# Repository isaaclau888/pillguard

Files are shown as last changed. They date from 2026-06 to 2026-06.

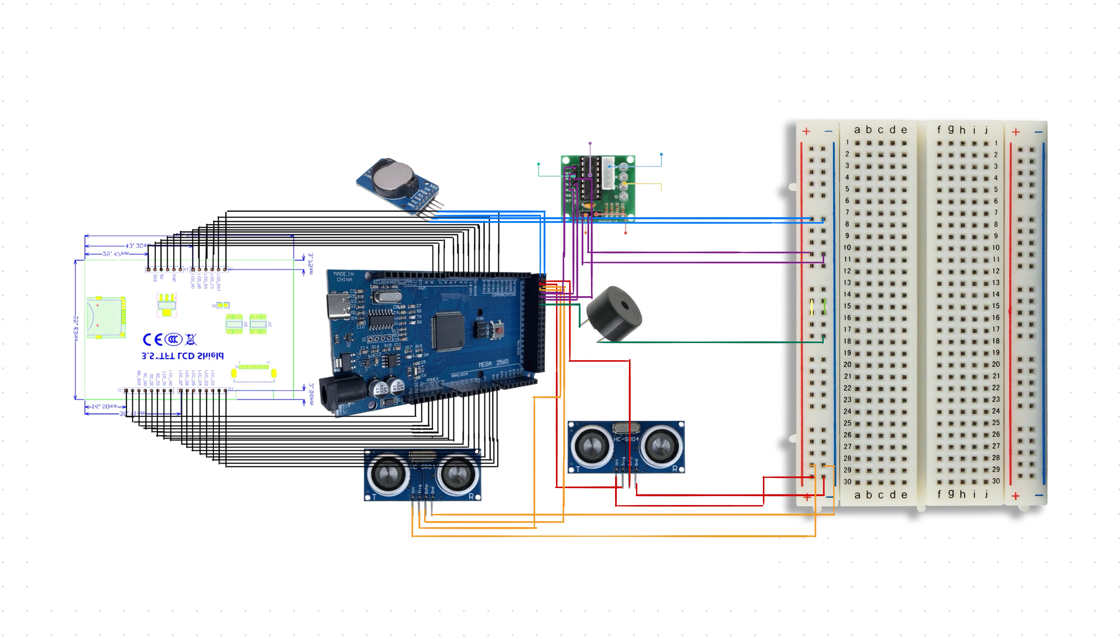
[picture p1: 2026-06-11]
PillGuard Wiring Diagram/PillGuard Wiring Diagram.jpg

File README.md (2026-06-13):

# PillGuard
Have you ever wanted to build a pill dispenser for yourself or your family?
For me, the answer is yes!

So here comes PillGuard, a pill dispenser that keeps track of and tells you when to take your pills. 
This is a completely open-source project. All the 3D parts and the BOM list are in the folders. You may customise my project. 

## How to build it
Please print all the 3D parts. <p>
螢幕截圖 2026-06-11 下午5 09 00 <p>
First, try placing the bottom part with the HC‑SR04 sensor in it. <p>

螢幕截圖 2026-06-11 下午5 09 55 <p>
Secondly, place the middle part with the 28BYJ-48 Stepper Motor + ULN2003 Driver and another HC‑SR04 sensor. <p>

螢幕截圖 2026-06-11 下午5 10 14 <p>
Thirdly, place the spinning system above the 28BYJ-48 Stepper Motor. <p>

螢幕截圖 2026-06-11 下午5 10 55 <p>
Last but not least, put the cover on top of the bottom part with the 3.5-inch screen and Arduino Mega 2560(The blue shaded place is where you place the screen and the Arduino Board).

# Wiring Diagram 
PillGuard Wiring Diagram

Screen: Just follow the diagram. <p>
DS3231 RTC (Real-Time Clock): VCC -> Breadboard (+) Red Rail, GND -> Breadboard (-) Blue Rail, Trig -> Arduino Mega 2560 Pin 20, Echo -> Arduino Mega 2560 Pin 21 <p>
HC-SR04(Cup Sensor): VCC -> Breadboard (+) Red Rail, GND -> Breadboard (-) Blue Rail, Trig -> Arduino Mega 2560 Pin 22, Echo -> Arduino Mega 2560 Pin 23 <p>
HC-SR04(Pill Drop Sensor): VCC -> Breadboard (+) Red Rail, GND -> Breadboard (-) Blue Rail, Trig -> Arduino Mega 2560 Pin 24, Echo -> Arduino Mega 2560 Pin 25 <p>
ULN2003(Steeper Motor Driver): VCC -> Breadboard (+) Red Rail, GND -> Breadboard (-) Blue Rail, IN1 -> Arduino Mega 2560 Pin 26, IN2 -> Arduino Mega 2560 Pin 27, IN3 -> Arduino Mega 2560 Pin 28, IN4 -> Arduino Mega 2560 Pin 29 <p>
Buzzer: Positive(+) -> Arduino Mega 2560 Pin 30, Negative(-) -> Breadboard (-) Blue Rail 

## Why this project actually exists
The reason why this project exists is that the HKDSE 2026 DAT SBA required students to make a  device for medication management and facilitation of medication taking.

Design Problem:
Design and make a device for medication management and facilitation of medication taking.
This device must satisfy the following requirements:
(a) Store at least five different pills separately, allow patients to set different dosages and medication times for each pill, and automatically dispense the required quantity of pills at the right time, for a period of at least one week;
(b) Provide medication reminders to patients in a variety of ways at a predetermined time until the patient confirms that the medication has been taken;
(c) Include a function that automatically provides the right amount of water to drink when it is time to take the medicine;
(d) Add a function that provides practical value to the patients. (For example, properly preserving the medicine.)

But I removed the part (c) feature in this project.

## How I made it
Guess how I made it. I made it by using Fusion 360, which is a completely free CAD app for students. The reason why I made this is that I want to make people not hate taking medicine. By using the dispenser, you can interact with it, making it more fun when you're ill. 

SBA_2026-Apr-05_04-36-30AM-000_CustomizedView2692837445_png

## How to use it?
The question you may ask is how to use this pill dispenser. To use this dispenser, you must set a timer on the app and select which medicine you're taking. For example, at 1 pm, I need to take 2 Panadol Pills. Then it will follow your instructions and do the task at 1 pm.

## Fallout Zine
PillGuard Fallout Zine

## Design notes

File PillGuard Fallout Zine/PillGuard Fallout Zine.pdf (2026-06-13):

# Time to takePILLS!

# PillGuard

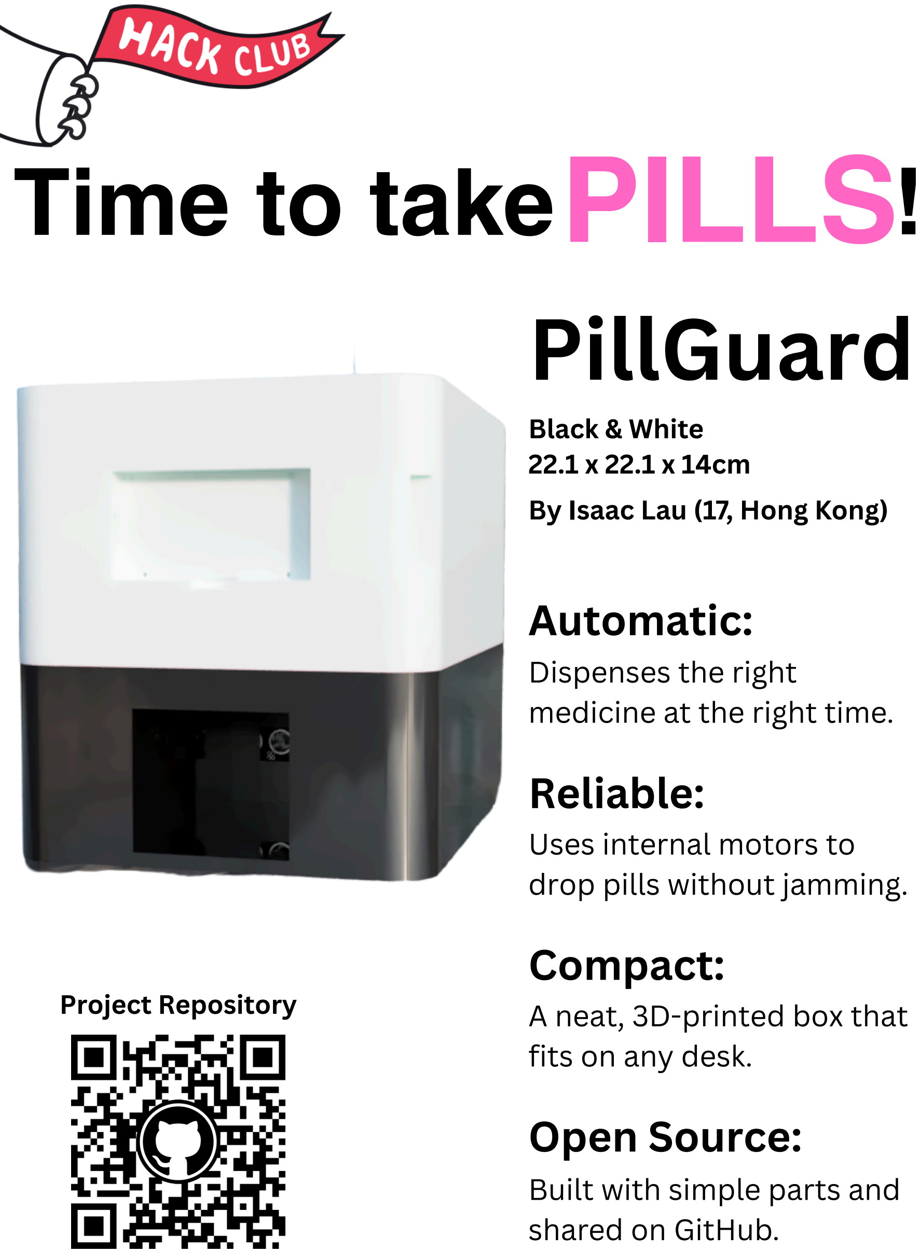
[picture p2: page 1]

Black & White

### 22.1 x 22.1 x 14cm

By Isaac Lau (17, Hong Kong)

Project Repository | Automatic:
Dispenses the right
medicine at the right time.

## Reliable:

Uses internal motors to
drop pills without jamming.

## Compact:

A neat, 3D-printed box that fits on any desk.

## Open Source:

Built with simple parts and shared on GitHub.

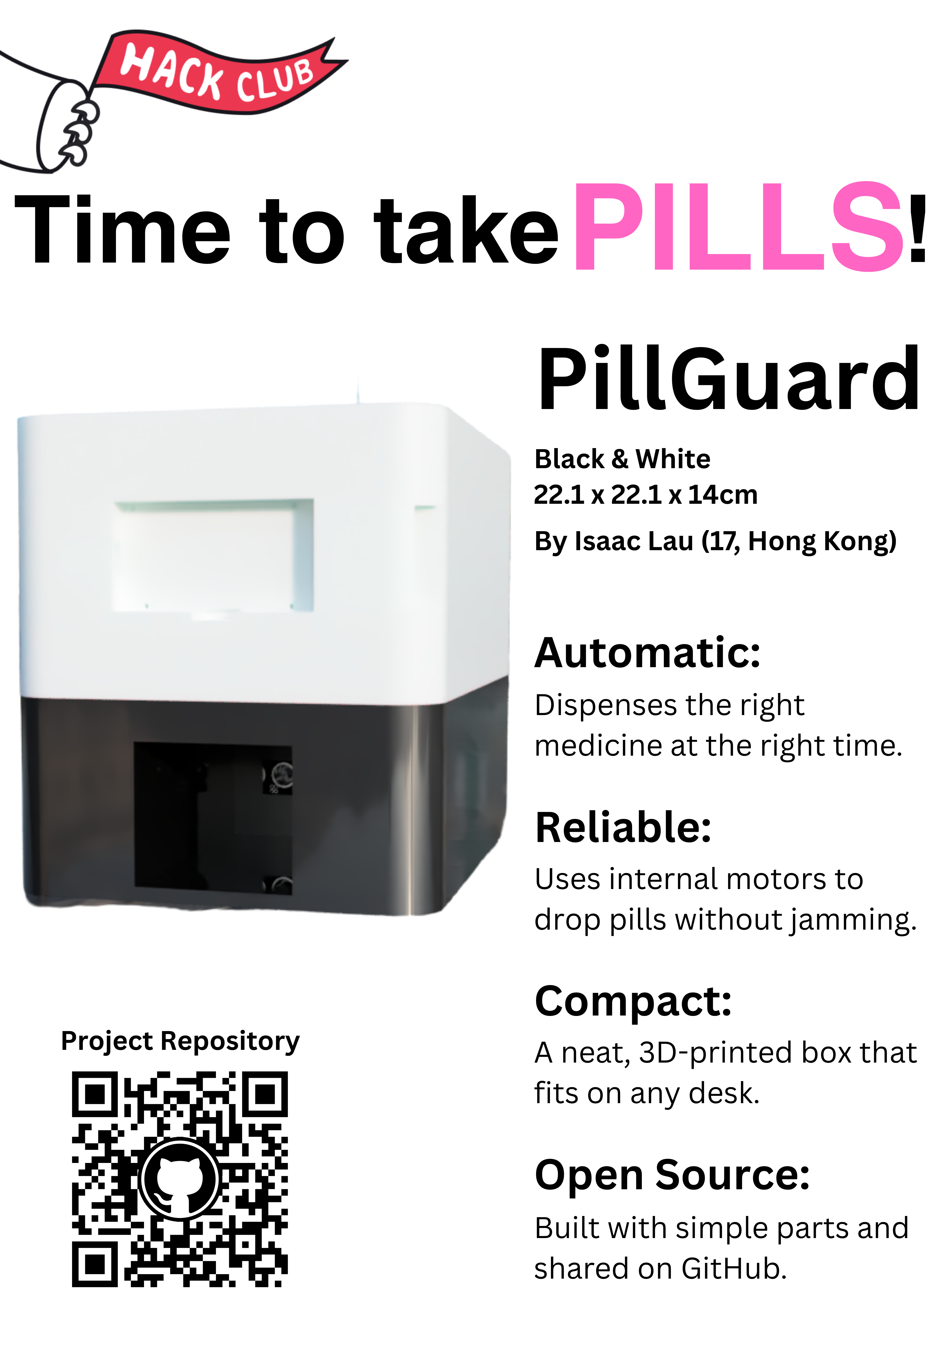
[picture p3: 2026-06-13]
PillGuard Fallout Zine/PillGuard Fallout Zine.png

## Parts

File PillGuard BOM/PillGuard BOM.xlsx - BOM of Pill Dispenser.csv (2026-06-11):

Description | Item | Usage Count | Purchase Quantity | Unit Price | Subtotal | Price(HKD) [$] | Price(RMB) [$] | Price(USD) [$] | Link | Additional description
Electrical Components
Arduino Mega 2560 R3 Type-C (CH340G) |  | 1 | 1 | $98.00 | $98.00 | $98.00 | $86.06 | $12.5 | https://hkstem.club/products/arduino-mega-2560?variant=47304128004391
3.5-inch TFT color screen module, 320x480 ultra-high-definition LCD screen |  | 1 | 1 | $43.32 | $43.32 | $43.32 | $37.50 | $5.53 | https://item.taobao.com/item.htm?id=619917753133
DS3231 RTC Module(Contains Battery) |  | 1 | 1 | $22.05 | $22.05 | $22.05 | $19.36 | $2.81 | https://detail.tmall.com/item.htm?ali_trackid=318_1513cffd14e591e2467183ac4e19fa0b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
28BYJ-48 Stepper Motor + ULN2003 Driver |  | 1 | 1 | $7.06 | $7.06 | $7.06 | $6.20 | $0.90 | https://item.taobao.com/item.htm?abbucket=10&id=682229618612&ns=1&priceTId=2100c90417752809138194116e0ce1&skuId=5076592483944&xxc=taobaoSearch
HC-SR04 Ultrasonic Sensor |  | 2 | 2 | $2.55 | $5.09 | $5.09 | $4.40 | $0.65 | https://item.taobao.com/item.htm?abbucket=10&id=863862858419&ns=1&priceTId=2100c90417752812554093218e0ce1&skuId=5686575112526&xxc=taobaoSearch
Active Buzzer(5V) |  | 1 | 1
Red LED + 220Ω Resistor |  | 2-3 | 2-3
Super Starter Kit (Active Buzzer(5V), Red LED + 220Ω Resistor, Breadboard + Jumper Wires Kit) |  |  |  | $120.71 | $120.71 | $120.71 | $106 | $15.40 | https://item.taobao.com/item.htm?abbucket=10&id=814569089511&ns=1&priceTId=2100c90417752817288805470e0ce1&skuId=5511429213951&xxc=taobaoSearch
 |  |  |  | Total |  | $296.23 | $259.52 | $37.79

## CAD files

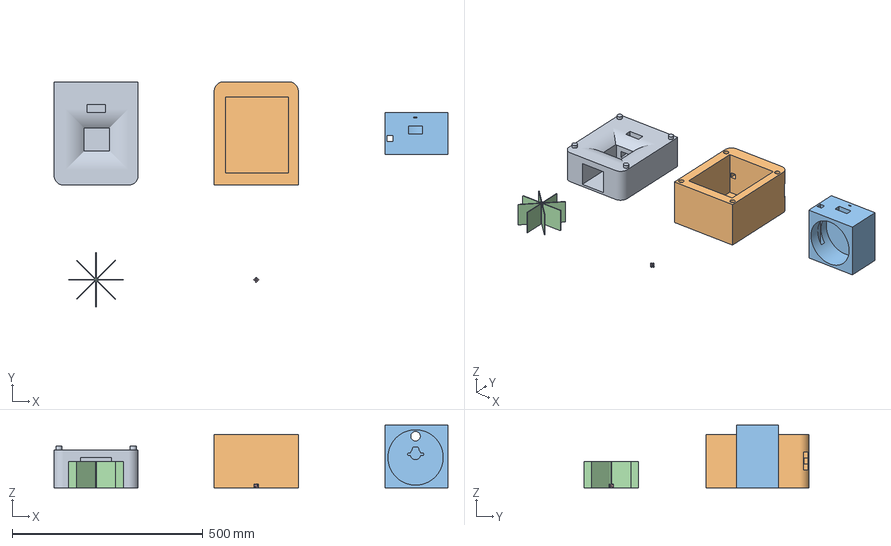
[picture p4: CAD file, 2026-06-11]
PillGuard 3mf File/PillGuard.3mf
1033.3 x 591.3 x 165.1 mm
PillGuard Bottom.step
PillGuard Cover.step
PillGuard Middle.step
PillGuard Spinning System.step
PillGuard Screws.step

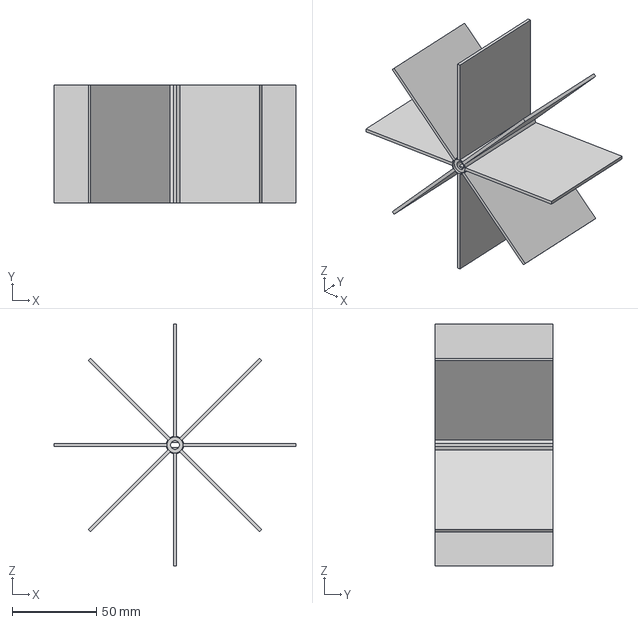
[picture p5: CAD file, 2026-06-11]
PillGuard STEP Files/PillGuard Spinning System.step
143.7 x 70.0 x 143.7 mm

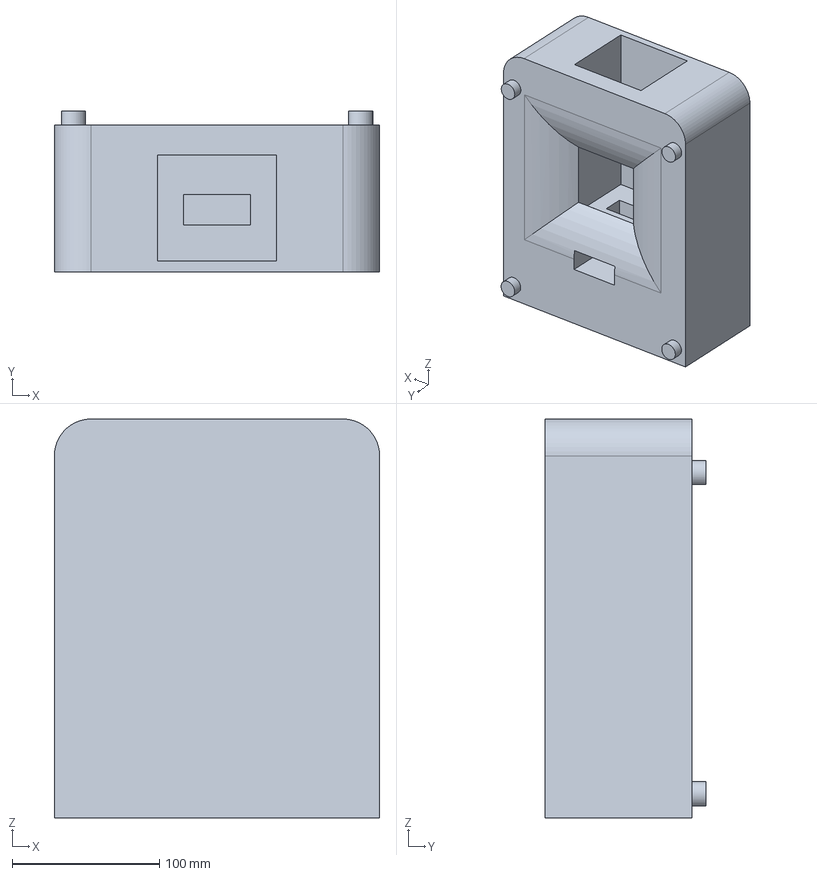
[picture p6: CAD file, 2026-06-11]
PillGuard STEP Files/PillGuard Bottom.step
220.9 x 109.5 x 270.9 mm

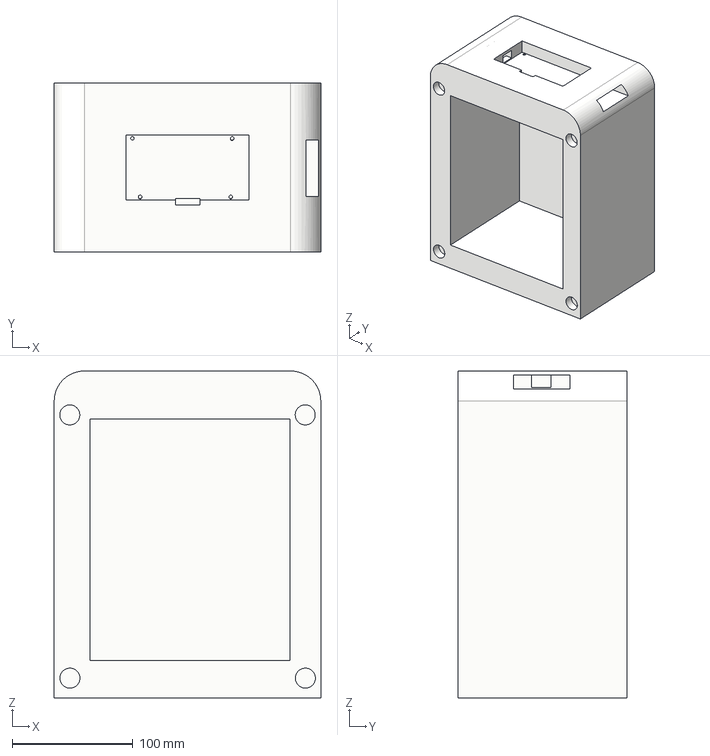
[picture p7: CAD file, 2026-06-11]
PillGuard STEP Files/PillGuard Cover.step
220.9 x 140.0 x 270.8 mm

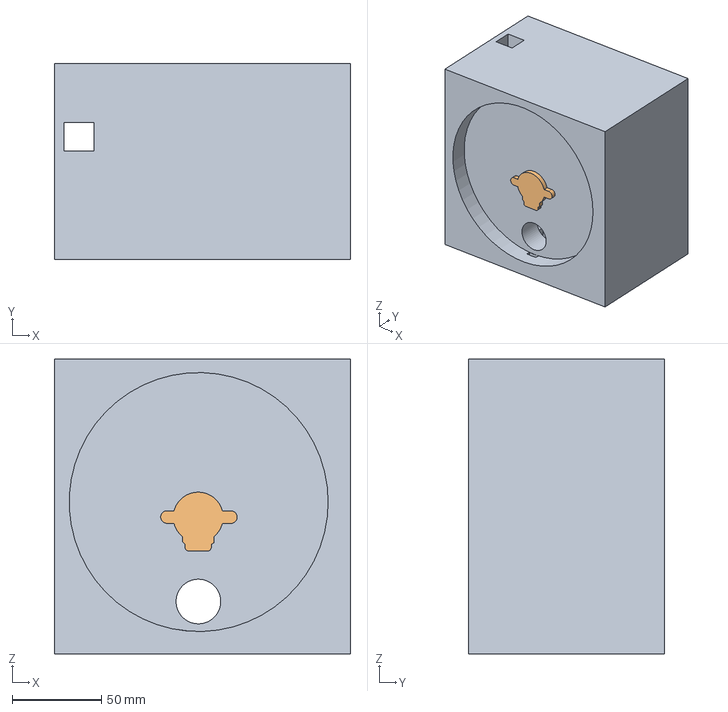
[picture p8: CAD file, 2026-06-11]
PillGuard STEP Files/PillGuard Middle.step
165.7 x 110.0 x 165.1 mm

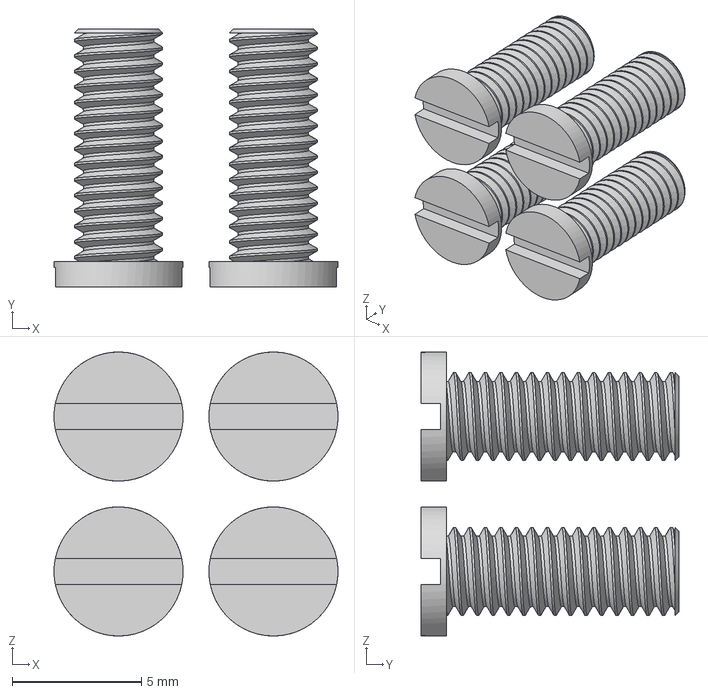
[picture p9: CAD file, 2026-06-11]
PillGuard STEP Files/PillGuard Screws.step
11.0 x 10.0 x 11.0 mm

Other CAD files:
PillGuard F3D/PillGuard.f3z

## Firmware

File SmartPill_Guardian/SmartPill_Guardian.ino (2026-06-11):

#include <Wire.h>
#include <RTClib.h>
#include <MCUFRIEND_kbv.h>
#include <Adafruit_GFX.h>
#include <TouchScreen.h>

#define TRIG_PIN_CUP 22
#define ECHO_PIN_CUP 23

#define TRIG_PIN_DROP 24
#define ECHO_PIN_DROP 25

#define STEPPER_IN1 26
#define STEPPER_IN2 27
#define STEPPER_IN3 28
#define STEPPER_IN4 29

#define BUZZER 30

#define YP A1 //Touch Y+
#define XM A2 //Touch X-
#define YM 7 //Touch Y-
#define XP 6 //Touch X+

MCUFRIEND_kbv tft;
RTC_DS3231 rtc;

TouchScreen ts = TouchScreen(XP, YP, XM, YM, 300);

int remainingPills[6] = {42, 35, 28, 40, 30, 25};
int dailyDose[6] = {2, 2, 1, 2, 1, 2};

unsigned long lastUpdate = 0;

void drawHomeScreen();
void updateTimeDisplay();
void checkLowStock();
void dispenseMedication(int compartment, int quantity);
void rotateToCompartment(int comp);
void stepMotor(long steps);
void showWarning(String msg);
void triggerReminder();
long readUltrasonicDistance(int trigPin, int echoPin);

void setup() {
  Serial.begin(9600);

  pinMode(TRIG_PIN_CUP, OUTPUT);
  pinMode(ECHO_PIN_CUP, INPUT);
  pinMode(TRIG_PIN_DROP, OUTPUT);
  pinMode(ECHO_PIN_DROP, INPUT);

  for(int i=22; i<=25; i++) {
    pinMode(i, OUTPUT); 
  }

  uint16_t ID = tft.readID();
  tft.begin(ID);
  tft.setRotation(1);
  tft.fillScreen(0x0000);

  if(!rtc.begin()) {
    Serial.println("RTC not found");
  }

  Serial.println("SmartPill Guardian Started");
  drawHomeScreen();
}

void loop() {
  if (millis() - lastUpdate > 1000) {
    updateTimeDisplay();
    checkLowStock();
    lastUpdate = millis();
  }

  DateTime now = rtc.now();
  if ((now.hour() == 8 || now.hour() == 14 || now.hour() == 20) && now.minute() == 0) {
    dispenseMedication(0, 2);
  }

  TSPoint p = ts.getPoint();
  if (p.z > 20) {
    tone(BUZZER, 1000, 100);
  }

  delay(50);
}

void drawHomeScreen() {
  tft.fillScreen(0x0000);
  tft.setTextColor(0xFFFF;
  tft.setTextSize(3);
  tft.setCursor(20, 20);
  tft.println("SmartPill");
  tft.setCursor(20, 60);
  tft.println("Guardian");
}

void updateTimeDisplay() {
  DateTime now = rtc.now();
  tft.fillRect(20, 120, 250, 40, 0x0000);

  tft.setTextSize(4);
  tft.setTextColor(0x07E0);
  tft.setCursor(40, 130);
  char buf[6];
  sprintf(buf, "%02d:%02d", now.hour(), now.minute());
  tft.print(buf);
}

void showWarning(String msg) {
  tft.fillRect(20, 200, 300, 60, 0xF800);
  tft.setTextColor(0xFFFF);
  tft.setTextSize(2);
  tft.setCursor(30, 220);
  tft.print(msg);
}

void dispenseMedication(int compartment, int quantity) {
  showWarning("Dispensing...");

  long cupDistance = readUltrasonicDistance(TRIG_PIN_CUP, ECHO_PIN_CUP);
  if (cupDistance > 10) {
    showWarning("Error: Place Cup!");
    triggerReminder();
    return;
  }

  rotateToCompartment(compartment);

  int count = 0;
  unsigned long startWait = millis();

  while (count < quantity) {
    stepMotor(40);

    long dropDistance = readUltrasonicDistance(TRIG_PIN_DROP, ECHO_PIN_DROP);
    if (dropDistance < 5) {
      count++;
      delay(300);
    }

    if (millis() - startWait > 15000) {
      showWarning("Dispenser Jammed!");
      triggerReminder();
      return;
    }
  }

  remainingPills[compartment] -= quantity;
  showWarning("Take Medicine Now");
  triggerReminder();
}

void rotateToCompartment(int comp) {
  long steps = comp * 341L;
  stepMotor(steps);
}

void stepMotor(long steps) {
  for (long i = 0; i < abs(steps); i++) {
    digitalWrite(STEPPER_IN1, HIGH); delay(3);
    digitalWrite(STEPPER_IN1, LOW);
    digitalWrite(STEPPER_IN2, HIGH); delay(3);
    digitalWrite(STEPPER_IN2, LOW);
    digitalWrite(STEPPER_IN3, HIGH); delay(3);
    digitalWrite(STEPPER_IN3, LOW); 
    digitalWrite(STEPPER_IN4, HIGH); delay(3);
    digitalWrite(STEPPER_IN4, LOW); 
  }
}

void triggerReminder() {
  for (int i = 0; i < 5; i++) {
    tone(BUZZER, 1500, 300);
    delay(500);
  }
}

void checkLowStock() {
  for (int i = 0; i < 6; i++) {
    float daysLeft = (float)remainingPills[i] / dailyDose [i];
    if (daysLeft <= 7.0) {
      showWarning("Low Stock! Refill Soon");
      triggerReminder();
      return;
    }
  }
}

long readUltrasonicDistance(int trigPin, int echoPin) {
  digitalWrite(trigPin, LOW);
  delayMicroseconds(2);
  digitalWrite(trigPin, HIGH);
  delayMicroseconds(10);
  digitalWrite(trigPin, LOW);

  long duration = pulseIn(echoPin, HIGH, 30000);
  long distance = duration * 0.034 / 2;
  return (distance == 0) ? 999 : distance;
}
